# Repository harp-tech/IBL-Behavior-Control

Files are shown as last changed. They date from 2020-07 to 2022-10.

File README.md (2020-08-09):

# IBL Behavior Control (IBL BC)

Repository for the IBL's new behavior control system, based on Harp technology.

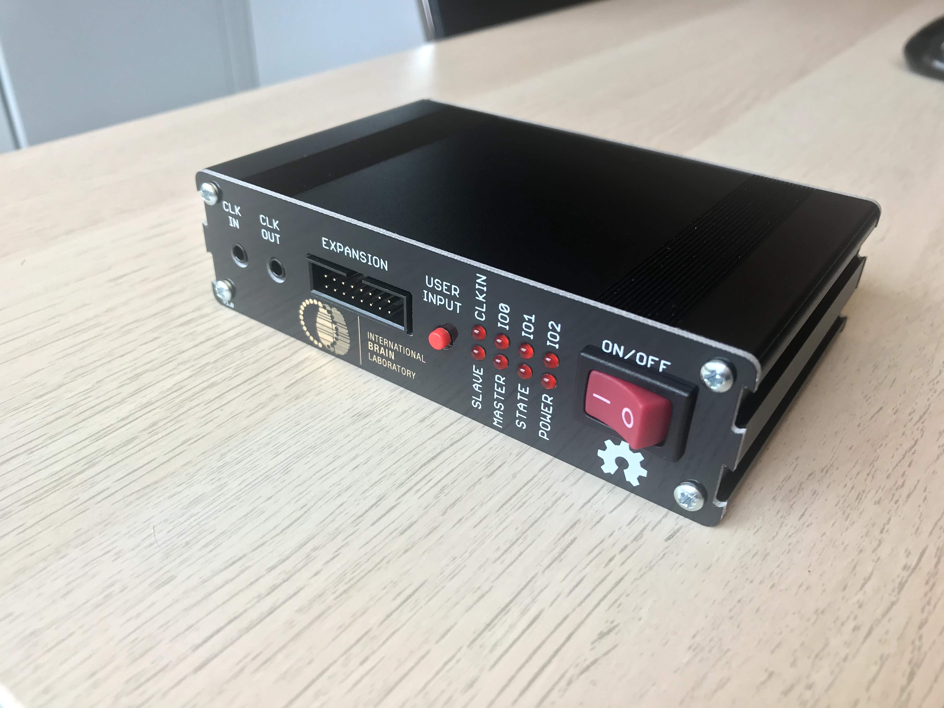
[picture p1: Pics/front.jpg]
DeviceFront


# Documentation

Manuals can be found in the folder *Manuals*

# Licensing

The code, designs, documentation, and photos available in this repository is free: you can redistribute it and/or modify it under the terms of the used license.
Each subdirectory will contain a license or, possibly, a set of licenses if it involves both hardware and software. Check files named LICENSE.

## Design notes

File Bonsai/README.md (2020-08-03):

# Bonsai - IBL Behavior Control Library

Bonsai Library for data acquisition and control of the IBL Behavior Control device.

For edits, you can use the Visual Studio Community Express.
(don't forget to install the .NET package)

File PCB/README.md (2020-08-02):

### Licensing
Copyright Filipe Carvalho 2020

<br />This work is licensed under a <a rel="license" href="http://creativecommons.org/licenses/by-nc-sa/3.0/igo/">Creative Commons Attribution-NonCommercial-ShareAlike 3.0 IGO License</a>.

If your are interested in obtaining a license to sell this device, please contact filipe@open-ephys.org

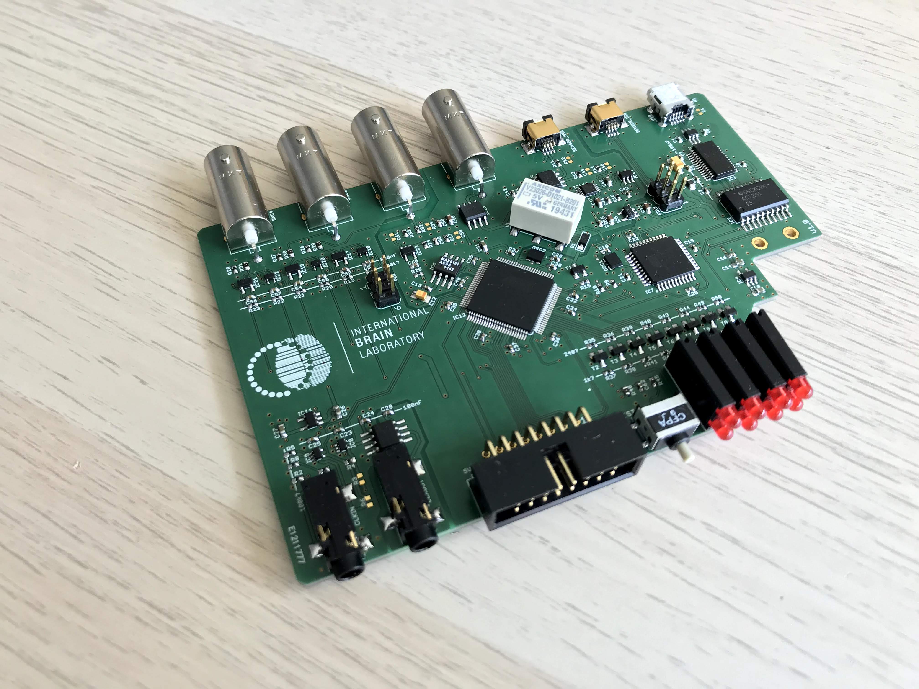
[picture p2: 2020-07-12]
Pics/pcb.jpg

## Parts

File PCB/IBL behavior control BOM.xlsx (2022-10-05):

OEPS PN | Schematic Name | Qtty. | Description | Type | Assembly | Manufacturer PN | Supplier | Supplier PN
OEPS IB1 001 | BNC1, BNC2, BNC3, BNC4 | 4 |  | TH | Yes | 0731000105 | Digi-key | WM5524-ND
OEPS IB1 002 | C1 | 1 | CAP CER 0402 4.7nF 100V ±10% X7R | SMD | Yes | GRM155R72A472KA01D | Mouser | 81-GRM155R72A472KA01
 | C10, C14, C26, C27, C31, C49 | 6 | CAP CER 0603 4.7uF 16V ±10% X5R | SMD | Yes | EMK107ABJ475KA-T | Mouser | 963-EMK107ABJ475KA-T
 | C11, C15, C41, C47, C48 | 5 | CAP CER 0603 10uF 25V ±10% X5R | SMD | Yes | GRM188R61E106KA73D | Mouser | 81-GRM188R61E106KA3D
 | C12 | 1 | SMD TAN 0805 20V 1uF ±10% ESR 6ohm | SMD | Yes | TPSR105K020R6000 | Mouser | 581-TPSR105K020R6000
 | C2, C3, C5, C7, C9, C13, C16, C17, C18, C19, C20, C21, C22, C23, C24, C25, C28, C29, C30, C32, C33, C34, C35, C36, C37, C38, C39, C40, C42, C43, C46, C50, C51, C52, C53, C54, C55, C56, C57, C60, C62 | 41 | CAP CER 0402 100nF 25V ±10% X7R | SMD | Yes | TMK105B7104KVHF | Mouser | 963-TMK105B7104KVHF
 | C4, C6 | 2 | CAP CER 0402 47pF 50V ±5% C0G | SMD | Yes | VJ0402A470JXACW1BC | Mouser | 77-VJ0402A470JXACBC
 | C44, C45, C58, C61 | 4 | - | SMD | DNP | - | - | -
 | C59 | 1 | CAP CER 0402 15nF 16V ±5% X7R | SMD | Yes | GRM155R71C153JA01D | Mouser | 81-GRM155R71C153JA1D
 | C8 | 1 | CAP TAN 1206 4.7uF 16V ±10% | SMD | Yes | TAJA475K016UNJ | Mouser | 581-TAJA475K016UNJ
 | CLKIN, CLKOUT | 2 | STEREO_JACK | SMD | Yes | 35RASMT2BHNTRX | Mouser | 502-35RASMT2BHNTRX
 | D1 | 1 | Schottky diode | SMD | Yes | 1N5819HW-7-F | Mouser | 621-1N5819HW-F
 | IC1 | 1 | ESD protection | SMD | Yes | USBLC6-2SC6Y | Mouser | 511-USBLC6-2SC6Y
 | IC10 | 1 | Digital Isolator | SMD | Yes | SI8610BC-B-IS | Mouser | 634-SI8610BC-B-IS
 | IC12 | 1 | Microcontroller | SMD | Yes | ATXMEGA128A1U-AU | Mouser | 556-ATXMEGA128A1U-AU
 | IC13, IC15 | 2 | OPAMP | SMD | Yes | AD8655ARZ | Mouser | 584-AD8655ARZ
 | IC14 | 1 | LDO 1.8V | SMD | Yes | TCR2EF18,LM(CT | Mouser | 757-TCR2EF18LMCT
 | IC16 | 1 | ADC | SMD | Yes | MCP33151D-10-E/MS | Mouser | 579-CP33151D-10-E/MS
 | IC17, IC19, IC21 | 3 | SINGLE BUS BUFFER GATE | SMD | Yes | SN74LVC1G125DBVR | Mouser | 595-SN74LVC1G125DBVR
 | IC2 | 1 | OCTAL BUFFER/DRIVER | SMD | Yes | SN74ACT241DW | Mouser | 595-SN74ACT241DW
 | IC23 | 1 | OPAMP | SMD | Yes | OPA365AIDBVR | Mouser | 595-OPA365AIDBVR
 | IC3 | 1 | USB TO SERIAL | SMD | Yes | FT232RL-REEL | Mouser | 895-FT232RL
 | IC4, IC11 | 2 | LDO 3.3V 200mA | SMD | Yes | TLV70033DDCR | Mouser | 595-TLV70033DDCR
 | IC5 | 1 | LDO 3.3V 250mA Ultra-Low-Noise | SMD | Yes | LP5907MFX-3.3/NOPB | Mouser | 595-LP5907MFX-3.3NPB
 | IC6 | 1 | REF 2.048V | SMD | Yes | MAX6162AESA+ | Mouser | 700-MAX6162AESA
 | IC7 | 1 | Microcontroller | SMD | Yes | ATXMEGA16A4U-AU | Mouser | 556-ATXMEGA16A4U-AU
 | IC8, IC9, IC18, IC20, IC22 | 5 | SINGLE BUS BUFFER GATE | SMD | Yes | M74VHC1GT126DT1G | Mouser | 863-M74VHC1GT126DT1G
 | L1 | 1 | 40ohms 100MHz 1.5A 0805 SMD | SMD | Yes | MI0805K400R-10 | Mouser | 875-MI0805K400R-10
 | LED0, LED1, LED2 | 4 | LED Circuit Board Indicator | TH | yes | 569-0111-100F | Mouser | 645-569-0111-100F
 | OSC1, OSC2 | 2 | CMOS Oscillator 32MHz 10ppm | SMD | Yes | DSC1001CI5-032.0000 | Mouser | 579-SC1001CI50320000
 | PDI, PDI1 | 2 | 2x3 HEADER | SMD | Yes | 67996-206HLF | Mouser | 649-67996-206HLF
 | R1 | 1 | RES SMD 0402 1MΩ ±1% 62.5mW | SMD | Yes | CR0402-FX-1004GLF | Mouser | 652-CR0402FX-1004GLF
 | R15, R35, R36, R39, R40, R43, R44, R49, R50 | 9 | RES SMD 0402 1kΩ ±1% 62.5mW | SMD | Yes | RC0402FR-071KL | Mouser | 603-RC0402FR-071KL
 | R2, R5, R8, R9, R10, R18, R19, R20, R21, R22, R23, R26, R27, R28 | 14 | RES SMD 0402 100kΩ 1% 100mW | SMD | Yes | ERJ-2RKF1003X | Mouser | 667-ERJ-2RKF1003X
 | R24, R45 | 2 | RES SMD 0402 10kΩ 0.5% 62.5mW | SMD | Yes | ERJ-2RHD1002X | Mouser | 667-ERJ-2RHD1002X
 | R29, R30, R31, R48 | 4 | RES SMD 0603 100Ω 1% 250mW | SMD | Yes | ESR03EZPF1000 | Mouser | 755-ESR03EZPF1000
 | R3, R6, R12, R34 | 4 | - | SMD | DNP | - | - | -
 | R32 | 1 | RES SMD 0402 24kΩ 1% 100mW | SMD | Yes | ERJ-2RKF2402X | Mouser | 667-ERJ-2RKF2402X
 | R33 | 1 | RES SMD 0402 16kΩ 1% 100mW | SMD | Yes | ERJ-2RKF1602X | Mouser | 667-ERJ-2RKF1602X
 | R37, R38, R41, R42, R46, R47, R51, R52 | 8 | RES SMD 0402 240Ω 1% 100mW | SMD | Yes | ERJ-2RKF2700X | Mouser | 667-ERJ-2RKF2700X
 | R4, R14, R17 | 3 | RES SMD 0402 0Ω | SMD | Yes | ERJ-2GE0R00X | Mouser | 667-ERJ-2GE0R00X
 | R7, R11, R13, R16, R25 | 5 | RES SMD 0402 10Ω 1% 100mW | SMD | Yes | ERJ-2RKF10R0X | Mouser | 667-ERJ-2RKF10R0X
 | SENSOR_ANA, SENSOR_DIG | 2 | Sensor plug | SMD | Yes | MQ172X-4PA(31) | Mouser | 798-MQ172X-4PA31
 | SV1 | 1 | CONN HEADER R/A 16POS 2.54MM | SMD | Yes | SBH11-PBPC-D08-RA-BK | Digi-key | S9179-ND
 | T1, T2, T3, T4, T5, T6, T7, T8, T9 | 9 | BJT NPN GP 45V 100mA | SMD | Yes | BC850C,215 | Mouser | 771-BC850C-T/R
 | TEST | 1 | Button | SMD | Yes | CFPA-1FB4-A2T | Digi-key | 563-1246-1-ND
 | U1 | 1 | Relay | SMD | Yes | V23026D1021B201 *X020 | Mouser | 655-V23026D1021XB
 | USB | 1 | Mini-USB connector | SMD | Yes | UX60-MB-5S8 | Mouser | 798-UX60-MB-5S8
 | - | 1 | Mini-USB cable | - | - | 88732-8502 | Mouser | 538-88732-8502
 | - | 1 | Enclosure | - | - | B5-080BK | Farnell | 1418616
 | - | 8 | Thread forming screws, M3, 6.5mm length | - | - |  | Fabory | 26760.029.006 (160411412)
 | - | 4 | Bumper Cylindrical Dome 9.53mm | - | - | SJ-5306-CLEAR-3000/CASE | DigiKey | SJ-5306-CLEAR-3000/CASE-ND

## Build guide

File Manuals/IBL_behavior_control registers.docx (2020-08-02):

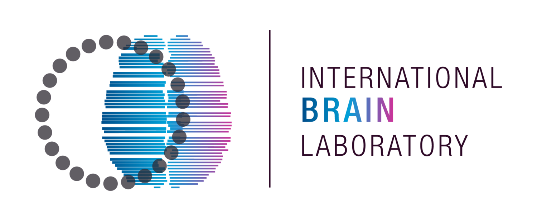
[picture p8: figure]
International Brain Laboratory

IBL Behavior Control - Device Registers Document Version 0.1

1. | Introduction
| The IBL Behavior Control device uses the most recent Harp core. This means that the comunication and synchronism of the device is covered by the Harp ecosistem. Therefore, the device uses registers to interface with the host computer. The user can use the available tools (Python and Bonsai (https://bonsai-rx.org/)) to communicate with the device and write & read from these registers. The purpose of this document is to explain the functionality of each register. If you have doubts, comments or suggestion, please provide them to filipe@open-ephys.org

2. | Registers
2.1 | List of Registers

Table 2-1. List of available Registers

Name | Type | Add | Brief Description
CONFIG | U16 | 32 | Configures the device
DATA_STREAM a) | I16 | 33 | Analog sensor, analog input, rotary encoder, and threshold events
INPUTS a) | U8 | 34 | Contains the state of the digital inputs (IO2) (IO1) (IO0)
INPUT_IO0_CONFIG | U8 | 35 | Configuration of port IO0 when used as digital input
INPUT_IO1_CONFIG | U8 | 36 | Configuration of port IO0 when used as digital input
INPUT_IO2_CONFIG | U8 | 37 | Configuration of port IO0 when used as digital input
OUTPUT_SET | U8 | 38 | Set to logic 1 the port IOx according to bit mask
OUTPUT_CLEAR | U8 | 39 | Clear to logic 0 the port IOx according to bit mask
OUTPUT_TOGGLE | U8 | 40 | Toggles the current logic port IOx according to bit mask
OUTPUT_WRITE | U8 | 41 | Write to the all ports (IO0, IO1 and IO1) at once
ANA_SENSOR_TH0_HIGH | U16 | 42 | Sets the higher threshold 0 for the analog sensor
ANA_SENSOR_TH0_HIGH_MS | U16 | 43 | Sets the number of milliseconds to consider a valid high threshold 0
ANA_SENSOR_TH0_LOW | U16 | 44 | Sets the lower threshold 0 for the analog sensor
ANA_SENSOR_TH0_LOW_MS | U16 | 45 | Sets the number of milliseconds to consider a valid low threshold 0
ANA_SENSOR_TH0_EVT_CONF | U8 | 46 | Configures what to do when the thresholds 0 are crossed
ANA_SENSOR_TH1_HIGH | U16 | 47 | Sets the higher threshold 1 for the analog sensor
ANA_SENSOR_TH1_HIGH_MS | U16 | 48 | Sets the number of milliseconds to consider a valid high threshold 1
ANA_SENSOR_TH1_LOW | U16 | 49 | Sets the lower threshold 1 for the analog sensor
ANA_SENSOR_TH1_LOW_MS | U16 | 50 | Sets the number of milliseconds to consider a valid low threshold 1
ANA_SENSOR_TH1_EVT_CONF | U8 | 51 | Configures what to do when the thresholds 1 are crossed
ANA_INPUT_TH0_HIGH | U16 | 52 | Sets the higher threshold 0 for the analog input
ANA_INPUT_TH0_HIGH_MS | U16 | 53 | Sets the number of milliseconds to consider a valid high threshold 0
ANA_INPUT_TH0_LOW | U16 | 54 | Sets the lower threshold 0 for the analog input
ANA_INPUT_TH0_LOW_MS | U16 | 55 | Sets the number of milliseconds to consider a valid low threshold 0
ANA_INPUT_TH0_EVT_CONF | U8 | 56 | Configures what to do when the thresholds 0 are crossed
ANA_INPUT_TH1_HIGH | U16 | 57 | Sets the higher threshold 1 for the analog input
ANA_INPUT_TH1_HIGH_MS | U16 | 58 | Sets the number of milliseconds to consider a valid high threshold 1
ANA_INPUT_TH1_LOW | U16 | 59 | Sets the lower threshold 1 for the analog input
ANA_INPUT_TH1_LOW_MS | U16 | 60 | Sets the number of milliseconds to consider a valid low threshold 1
ANA_INPUT_TH1_EVT_CONF | U8 | 61 | Configures what to do when the thresholds 1 are crossed
ENCODER_TH0_HIGH | I16 | 62 | Sets the higher threshold 0 for the encoder
ENCODER_TH0_HIGH_MS | U16 | 63 | Sets the number of milliseconds to consider a valid high threshold 0
ENCODER_TH0_LOW | I16 | 64 | Sets the lower threshold 0 for the encoder
ENCODER_TH0_LOW_MS | U16 | 65 | Sets the number of milliseconds to consider a valid low threshold 0
ENCODER_TH0_EVT_CONF | U8 | 66 | Configures what to do when the thresholds 0 are crossed
ENCODER_TH1_HIGH | I16 | 67 | Sets the higher threshold 1 for the encoder
ENCODER_TH1_HIGH_MS | U16 | 68 | Sets the number of milliseconds to consider a valid high threshold 1
ENCODER_TH1_LOW | I16 | 69 | Sets the lower threshold 1 for the encoder
ENCODER_TH1_LOW_MS | U16 | 70 | Sets the number of milliseconds to consider a valid low threshold 1
ENCODER_TH1_EVT_CONF | U8 | 71 | Configures what to do when the thresholds 1 are crossed
TH_ENABLE_EVENTS | U8 | 72 | Enables each event from the thresholds
WRITE_AO | U16 | 73 | Writes to the analog output available on port AO
ENCODER | I16 | 74 | Value of the digital encoder (write this register to 0 to reset the encoder)

a) This register is read only. Writing to this register will issue an error.
2.1.1 | CONFIG

Bit | 15 | 14 | 13 | 12 | 11 | 10 | 9 | 8
| - | DATA_1KHz | DATA_QUIET | IO2_TO_OUTPUT | IO2_TO_INPUT | IO1_TO_OUTPUT | IO1_TO_INPUT | IO0_TO_OUTPUT
Bit | 7 | 6 | 5 | 4 | 3 | 2 | 1 | 0
| IO0_TO_INPUT | COM_TO_TIMESTAMP | COM_TO_MAIN | EN_AI | ANA_INTERNAL_TO_A0 | ANA_SENSOR_TO_A0 | SYNC_TO_SLAVE | SYNC_TO_MASTER

This register is used to configure the device. As a good practice, this register should be the first one to be written.

When writing to one of these bits, the configuration will be executed, i.e., there’s no need to write all the necessary bits at once.

Example: We want to configure the device to enable the Harp Timestamp output, configure the digital IO1 to output and have data streamed at 1 KHz. We have two options (the end result is exactly the same):

Option a) Write all configuration at once

#define B_SYNC_TO_MASTER (1<<0)
#define B_IO1_TO_OUTPUT (1<<10)
#define B_DATA_1KHz (1<<14)

write_register(R_CONFIG, B_SYNC_TO_MASTER | B_IO1_TO_OUTPUT | B_DATA_1KHz);

Option b) Write each configuration individually

write_register(R_CONFIG, B_SYNC_TO_MASTER);
write_register(R_CONFIG, B_IO1_TO_OUTPUT);
write_register(R_CONFIG, B_DATA_1KHz);

- Bits 0 – SYNC_TO_MASTER

The device outputs the internal clock sync into CLKOUT.

Another Harp device can be connected to this bus in order to share the same timestamp base.

- Bit 1 – SYNC_TO_SLAVE

Setting this bit to 1, the device receives the clock sync trough CLKIN and daisy chain it into CLKOUT (to synchronize another Harp device).

- Bit 2 – ANA_SENSOR_TO_A0

Setting this bit to 1, the analog sensor voltage value is sent to port AO. User can use this port to monitor the analog sensor.

- Bit 3 – ANA_INTERNAL_TO_A0

Setting this bit to 1, the internal analog generator is sent to port AO. User can use the register WRITE_A0 to output an analog voltage on this port.

- Bit 4 – EN_AI

Setting this bit to 1, enables the analog input reading on port AI and disables the digital input/output circuitry.

This means that this port is used as an analog port.

- Bit 5 – COM_TO_MAIN

The device has two microcontrollers running internally. One is dedicated to behavior and the other to timing synchronism.

When this bit is set to logic 1, the USB communication is made with the behavior microcontroller.

This feature is used only for firmware update purposes.

- Bit 6 – COM_TO_TIMESTAMP

When this bit is set to logic 1, the USB communication is made with the timing synchronism microcontroller.

This feature is used only for firmware update purposes.

- Bit 7 – IO0_TO_OUTPUT

Setting this bit to 1, configures the port IO0 to be used as a digital output.

- Bit 8 – IO0_TO_INPUT

Setting this bit to 1, configures the port IO0 to be used as a digital input.

- Bit 9 – IO1_TO_OUTPUT

Setting this bit to 1, configures the port IO1 to be used as a digital output.

- Bit 10 – IO1_TO_INPUT

Setting this bit to 1, configures the port IO1 to be used as a digital input.

- Bit 11 – IO2_TO_OUTPUT

Setting this bit to 1, configures the port IO2 to be used as a digital output.

- Bit 12 – IO2_TO_INPUT

Setting this bit to 1, configures the port IO3 to be used as a digital input.

- Bit 13 – DATA_QUIET

The register DATA_STREAM can be sent to the host computer using one of two options. Sent at a frequency of 1000 samples/second or sent only when any of the thresholds is crossed (widely used to screen synchronization).

Setting this bit to 1, configures the device to send the DATA_STREAM register only when a threshold is crossed (on any of the two ways, rising or falling).

- Bit 14 – DATA_1KHz

Setting this bit to 1, configures the device to send the DATA_STREAM register at a frequency of 1000 samples/second.
2.1.2 | DATA_STREAM

This register is an array composed of four words with 16 bits signed.

DATA_STREAM[0] Analog reading from the analog sensor input

DATA_STREAM[1] Analog reading from the AI0 input

DATA_STREAM[2] Rotary encoder’s position

DATA_STREAM[3] Contains a bitmask reflecting the thresholds state

Below, is the DATA_STREAM[3] bitmask.

Bit | 15-6 | 5 | 4 | 3 | 2 | 1 | 0
| - | ENCTH1 | ENCTH0 | AITH1 | AITH0 | ASTH1 | ASTH0

- Bits ASTHx

If this bit is set to 1, it means that the reading of analog sensor input is above the threshold ANA_SENSOR_THx_HIGH for the time configured in ANA_SENSOR_THx_HIGH.

If this bit is clear to 0, it means that the reading of analog sensor input is below the threshold ANA_SENSOR_THx_LOW for the time configured in ANA_SENSOR_THx_LOW.

This bit is always read as 0.

- Bits AITHx

If this bit is set to 1, it means that the reading of analog input is above the threshold ANA_INPUT_THx_HIGH for the time configured in ANA_INPUT_THx_HIGH.

If this bit is clear to 0, it means that the reading of analog input is below the threshold ANA_INPUT_THx_LOW for the time configured in ANA_INPUT_THx_LOW.

- Bits ENCTHx

If this bit is set to 1, it means that the reading of the encoder is above the threshold ENCODER_THx_HIGH for the time configured in ENCODER_THx_HIGH.

If this bit is clear to 0, it means that the reading of the encoder is below the threshold ENCODER_THx_LOW for the time configured in ENCODER_THx_LOW.
2.1.3 | INPUTS
| This register is sent to the host computer according to registers INPUT_IOx_CONFIG. Bit 7 6 5 4 3 2 1 0 - - - - - IO2 IO1 IO0 - Bits 0 – IO0 Contains the digital state of the port IO0. - Bits 1 – IO1 Contains the digital state of the port IO1. - Bits 2 – IO2 Contains the digital state of the port IO2.
2.1.4 | INPUT_IOx_CONFIG It is good practices to keep the bandwidth of the device as low as possible. If what matters is the transition from logic 0 to logic 1 (a camera’s strobe, for instance), the option 1 should be used, and the device will ignore the logic 1 to logic 0 transition.
| Bit 7 6 5 4 3 2 1 0 - - - - - - INPUT_OPTIONS [1:0] - Bits 1:0 – INPUT_OPTIONS [1:0] INPUT_OPTIONS [1:0] Configuration 0 Port IOx input is not used 1 Port IOx input is sensitive to both edges 2 Reserved 3 Reserved
2.1.5 | OUTPUT_SET OUTPUT_CLEAR OUTPUT_TOGGLE OUTPUT_WRITE
| Bit 7 6 5 4 3 2 1 0 - - - - - IO2 IO1 IO0 The action is taking according to the bit mask. Examples: Set only Port IO0 to logic 1: OUTPUT_SET = (1<<0) Set only Port IO2 to logic 1: OUTPUT_SET = (1<<2) Set both Port IO1 and IO2 to logic 1: OUTPUT_SET = (1<<1) | (1<<2) Clear only Port IO1 to logic 0: OUTPUT_CLEAR = (1<<1) Toggle the current logic state of Port IO1: OUTPUT_TOGGLE = (1<<1) Write IO0 to logic 0, IO1 to logic 1 and IO2 to logic 1 (all at the same time): OUTPUT_WRITE = (1<<1) | (1<<2)
2.1.6 | ANA_SENSOR_THx_EVT_CONF ANA_INPUT_THx_EVT_CONF ECNODER_THx_EVT_CONF This register configures if the threshold result is show in the digital outputs.
| Bit 7 6 5 4 3 2 1 0 - - - - - - TH_OPTIONS [1:0] - Bits 1:0 – TH_OPTIONS [1:0] TH_OPTIONS [1:0] Configuration 0 Don’t output the threshold 1 a) Threshold result on IO0 2 Threshold result on IO1 3 Threshold result on IO2 a) This option is not valid when used on registers ANA_INPUT_THx_EVT_CONF.
2.1.7 | TH_ENABLE_EVENTS
| This register allows the user to disable the non-used thresholds. It is recommended to disable the nonused ones! Bit 7 6 5 4 3 2 1 0 - - ENCTH1 ENCTH0 AITH1 AITH0 ASTH1 ASTH0 - Bits 5:0 Writing to logic 0 disables the correspondent threshold. Writing to logic 1 enables the correspondent threshold.

| Version Control
| V0.1 First version released.

IBL Behavior Control | Device Registers 5

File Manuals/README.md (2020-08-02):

### Licensing
Copyright Filipe Carvalho 2020

<br />Este trabalho está licenciado com uma Licença <a rel="license" href="http://creativecommons.org/licenses/by/4.0/">Creative Commons - Atribuição  4.0 Internacional</a>.

#### You are free to:
*Share* — copy and redistribute the material in any medium or format
*Adapt* — remix, transform, and build upon the material for any purpose, even commercially.

#### Under the following terms:
*Attribution* — You must give appropriate credit, provide a link to the license, and indicate if changes were made. You may do so in any reasonable manner, but not in any way that suggests the licensor endorses you or your use.

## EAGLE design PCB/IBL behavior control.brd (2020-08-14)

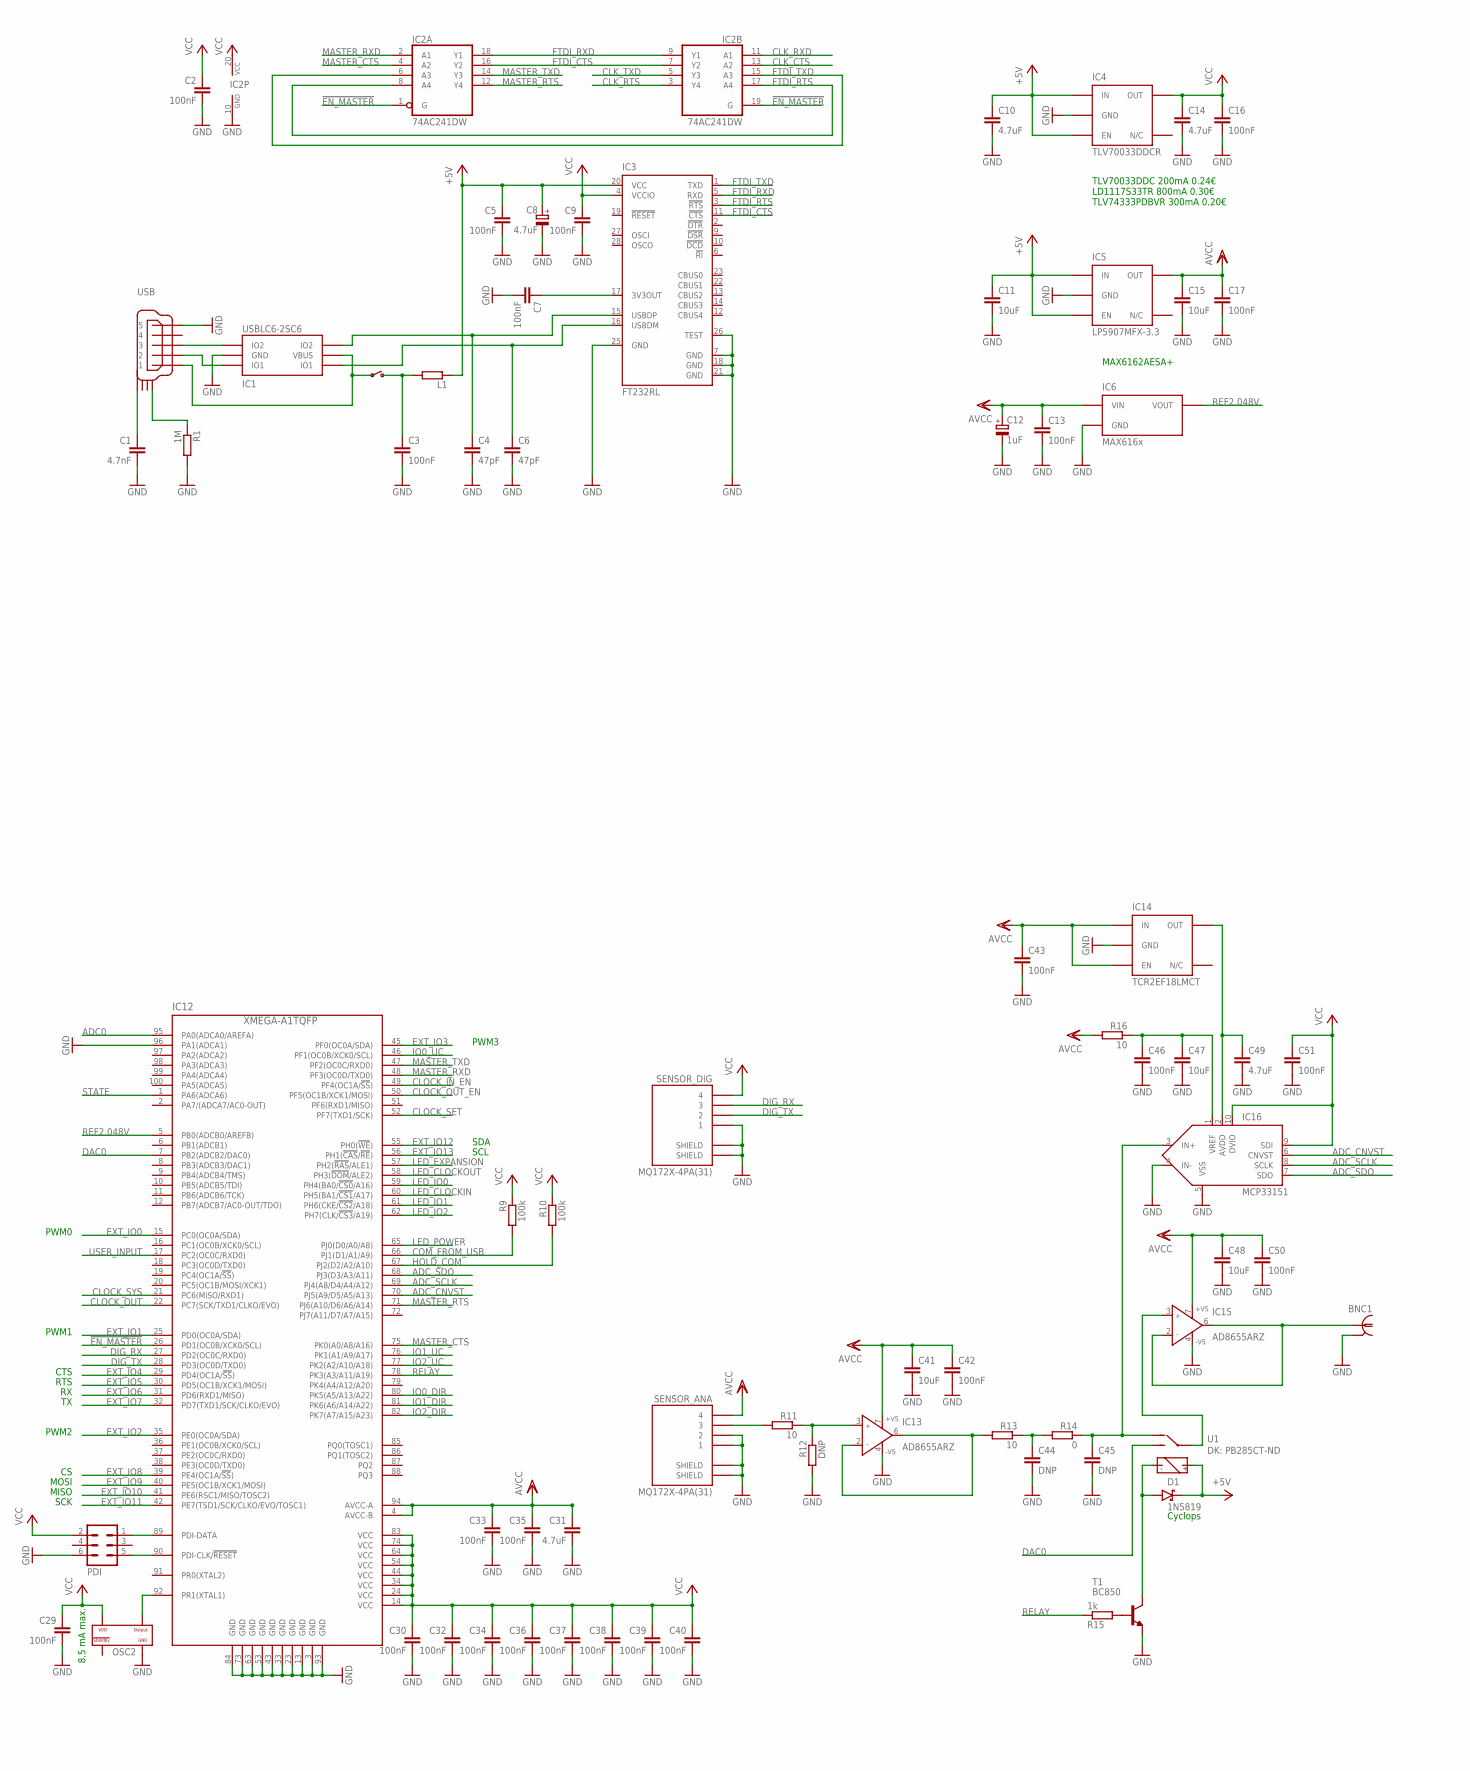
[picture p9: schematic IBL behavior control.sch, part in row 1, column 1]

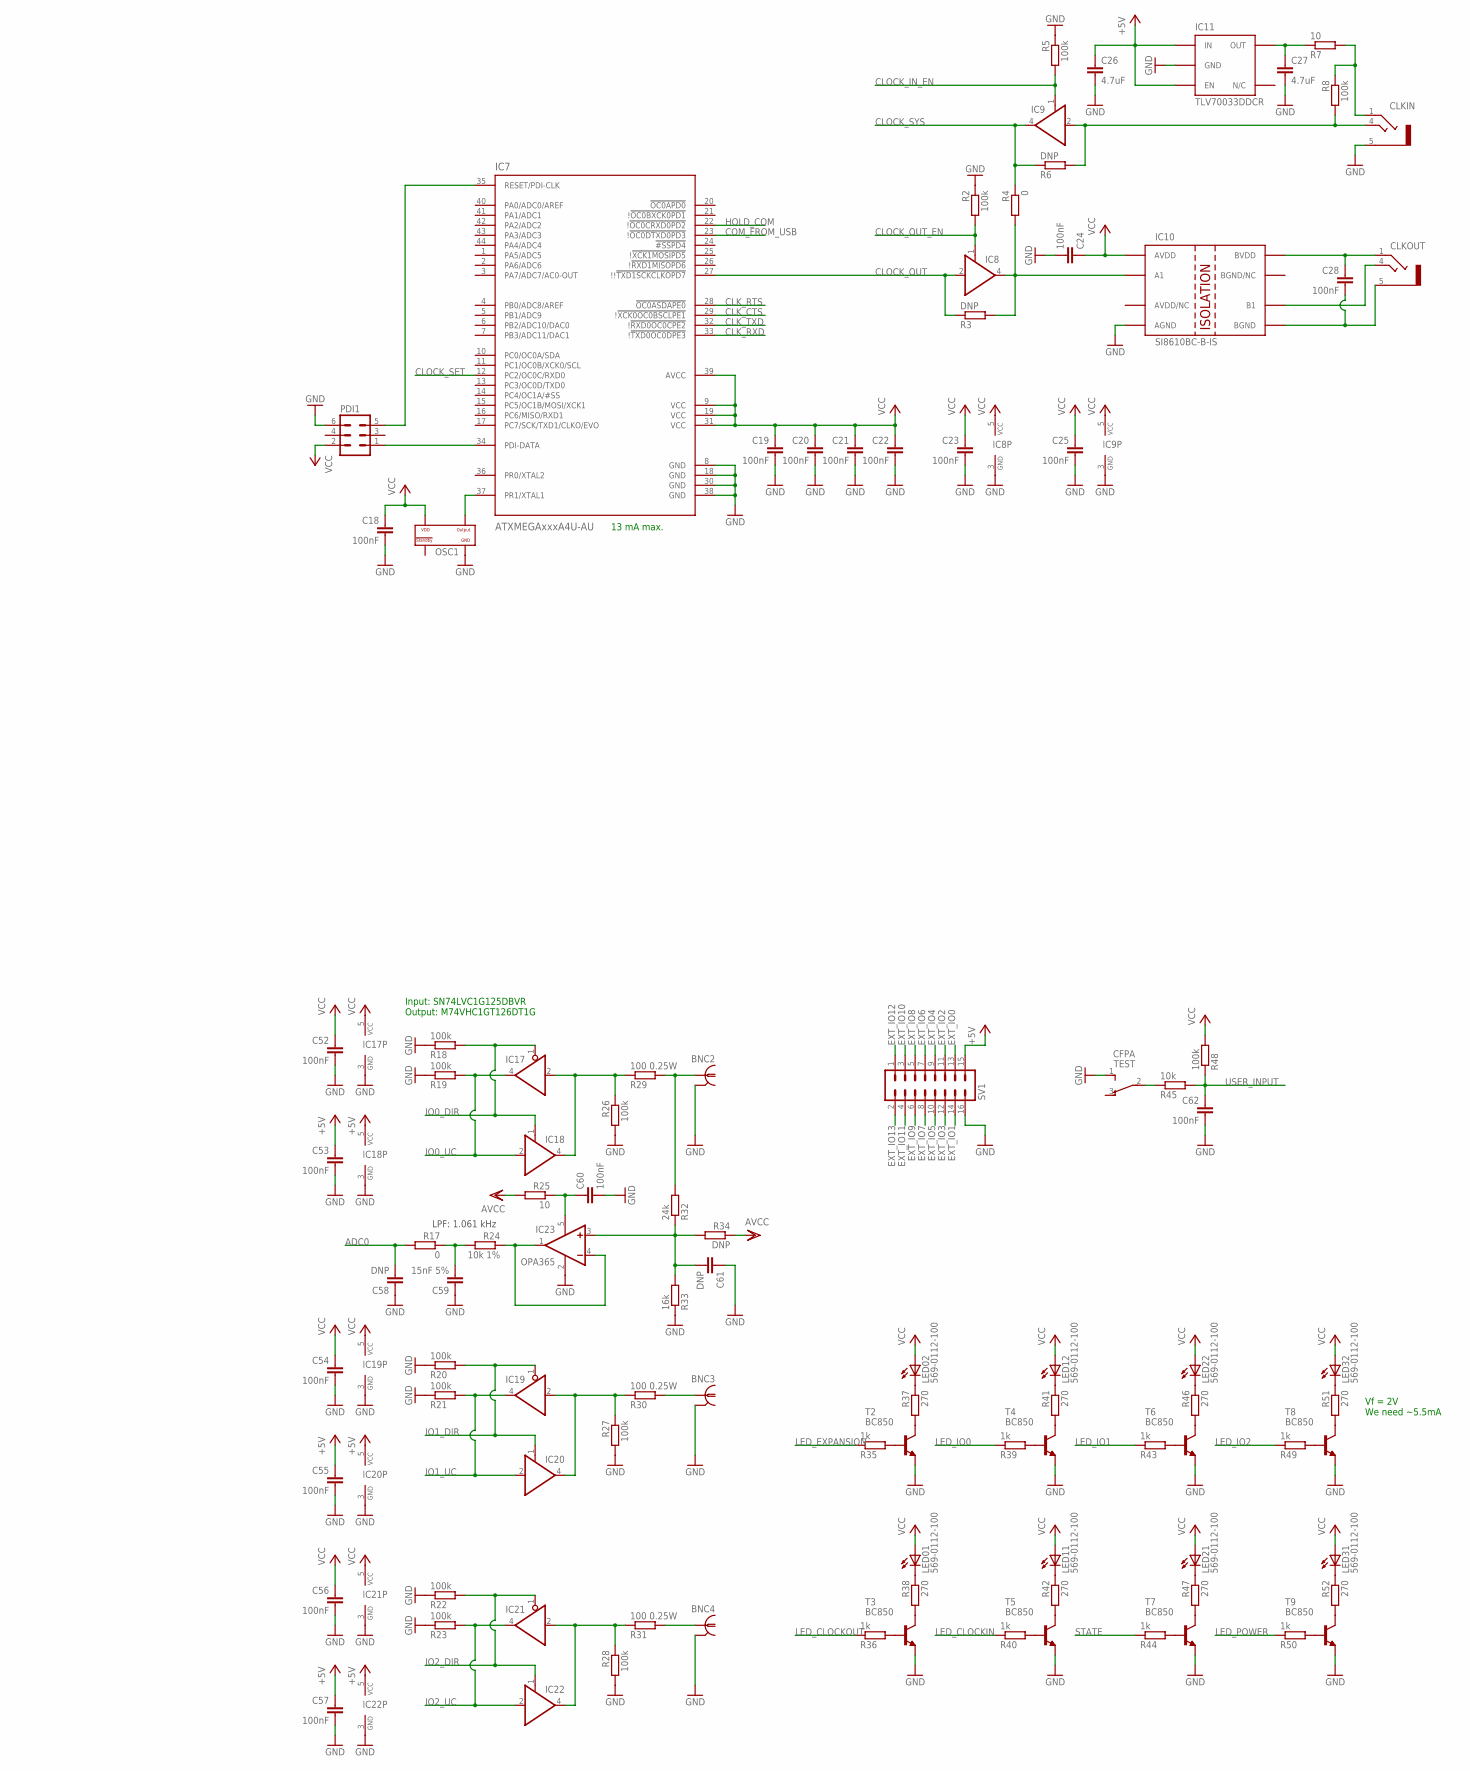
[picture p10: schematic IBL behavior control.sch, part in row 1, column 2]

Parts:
BNC1, BNC2, BNC3, BNC4: BNC_0731000105; 0731000105
C1: 4.7nF; C0402
C2, C3, C5, C7, C9, C13, C16, C17, C18, C19, C20, C21, C22, C23, C24, C25, C28, C29, C30, C32, C33, C34, C35, C36, C37, C38, C39, C40, C42, C43, C46, C50, C51, C52, C53, C54, C55, C56, C57, C60, C62: 100nF; C0402
C4, C6: 47pF; C0402
C8: 4.7uF; A/3216-18W
C10, C14, C26, C27, C31, C49: 4.7uF; C0603
C11, C15, C41, C47, C48: 10uF; C0603
C12: 1uF; R/2012-12R
C44, C45, C58, C61: DNP; C0402
C59: 15nF 5%; C0402
CLKIN: STEREO_JACK; 35RASMT2BHNTRX
CLKOUT: STEREO_JACK; 35RASMT2BHNTRX
D1: 1N5819; SOD123
IC1: USBLC6-2SC6; SOT23-6L
IC2: 74AC241DW; SO20W
IC3: FT232RL; SSOP28
IC4, IC11: TLV70033DDCR; TSOT23-5
IC5: LP5907MFX-3.3; TSOT23-5
IC6: MAX616x; SO-08
IC7: ATXMEGAxxxA4U-AU; QFP80P1200X1200X120-44N
IC8, IC9, IC18, IC20, IC22: 74AHC1G126DCK; SC70-5
IC10: SI8610BC-B-IS; SO-08
IC12: XMEGA-A1TQFP; TQFP100
IC13, IC15: AD8655ARZ; SO8
IC14: TCR2EF18LMCT; TSOT23-5
IC16: MCP33151; MSOP10
IC17, IC19, IC21: 74AHC1G125DBV; SOT23-5
IC23: OPA365; SOT23-5
L1: ???; R0805
LED0, LED1, LED2, LED3: 569-0112-100; 569-011X-X00_LED_ARRAY
OSC1, OSC2: OSCILLATOR; OSCILLATOR_3.2X2.5
PDI, PDI1: MA03-2
R1: 1M; R0402
R2, R5, R8, R9, R10, R18, R19, R20, R21, R22, R23, R26, R27, R28, R48: 100k; R0402
R3, R6, R12, R34: DNP; R0402
R4, R14, R17: 0; R0402
R7, R11, R13, R16, R25: 10; R0402
R15, R35, R36, R39, R40, R43, R44, R49, R50: 1k; R0402
R24: 10k 1%; R0402
R29, R30, R31: 100 0.25W; R0603
R32: 24k; R0402
R33: 16k; R0402
R37, R38, R41, R42, R46, R47, R51, R52: 270; R0402
R45: 10k; R0402
SENSOR_ANA: MQ172X-4PA(31)
SENSOR_DIG: MQ172X-4PA(31)
SV1: ML16L
T1, T2, T3, T4, T5, T6, T7, T8, T9: BC850; SOT23
TEST: CFPA
U1: DK: PB285CT-ND; RELAY
USB: USB_MINI_B; 240-0002-1

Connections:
5VSWITCH: C3.1, L1.2
5VUSB: IC1.P$5 (VBUS), USB.P$1 (1)
!EN_MASTER: IC2.1 (G), IC2.19 (G), IC12.26 (PD1(OC0B/XCK0/SCL))
+5V: C5.1, C8.+, C10.1, C11.1, C26.1, C53.1, C55.1, C57.1, D1.C, IC3.20 (VCC), IC4.1 (IN), IC4.3 (EN), IC5.1 (IN), IC5.3 (EN), IC11.1 (IN), IC11.3 (EN), IC18.5 (VCC), IC20.5 (VCC), IC22.5 (VCC), L1.1, SV1.15, U1.3 (R+)
ADC0: C58.2, IC12.95 (PA0(ADCA0/AREFA)), R17.2
ADC_CNVST: IC12.70 (PJ5(A9/D5/A5/A13)), IC16.6 (CNVST)
ADC_SCLK: IC12.69 (PJ4(A8/D4/A4/A12)), IC16.8 (SCLK)
ADC_SDO: IC12.68 (PJ3(D3/A3/A11)), IC16.7 (SDO)
CLK_CTS: IC2.13 (A2), IC7.29 (!!XCK0OC0BSCLPE1)
CLK_RTS: IC2.3 (Y4), IC7.28 (!OC0ASDAPE0)
CLK_RXD: IC2.11 (A1), IC7.33 (!!TXD0OC0DPE3)
CLK_TXD: IC2.5 (Y3), IC7.32 (!!RXD0OC0CPE2)
CLOCK_IN_EN: IC9.1 (OE), IC12.49 (PF4(OC1A/!SS!)), R5.2
CLOCK_OUT: IC7.27 (!!!TXD1SCKCLKOPD7), IC8.2 (I), IC12.22 (PC7(SCK/TXD1/CLKO/EVO)), R3.1
CLOCK_OUT_EN: IC8.1 (OE), IC12.50 (PF5(OC1B/XCK1/MOSI)), R2.2
CLOCK_SET: IC7.12 (PC2/OC0C/RXD0), IC12.52 (PF7(TXD1/SCK))
CLOCK_SYS: IC9.4 (O), IC12.21 (PC6(MISO/RXD1)), R4.1, R6.1
COM_FROM_USB: IC7.23 (!!OC0DTXD0PD3), IC12.66 (PJ1(D1/A1/A9)), R9.2
DAC0: IC12.7 (PB2(ADCB2/DAC0)), U1.10 (NO)
DIG_RX: IC12.27 (PD2(OC0C/RXD0)), SENSOR_DIG.3
DIG_TX: IC12.28 (PD3(OC0D/TXD0)), SENSOR_DIG.2
EXT_IO0: IC12.15 (PC0(OC0A/SDA)), SV1.13
EXT_IO1: IC12.25 (PD0(OC0A/SDA)), SV1.14
EXT_IO2: IC12.35 (PE0(OC0A/SDA)), SV1.11
EXT_IO3: IC12.45 (PF0(OC0A/SDA)), SV1.12
EXT_IO4: IC12.29 (PD4(OC1A/!SS!)), SV1.9
EXT_IO5: IC12.30 (PD5(OC1B/XCK1/MOSI)), SV1.10
EXT_IO6: IC12.31 (PD6(RXD1/MISO)), SV1.7
EXT_IO7: IC12.32 (PD7(TXD1/SCK/CLKO/EVO)), SV1.8
EXT_IO8: IC12.39 (PE4(OC1A/!SS!)), SV1.5
EXT_IO9: IC12.40 (PE5(OC1B/XCK1/MOSI)), SV1.6
EXT_IO10: IC12.41 (PE6(RSC1/MISO/TOSC2)), SV1.3
EXT_IO11: IC12.42 (PE7(TSD1/SCK/CLKO/EVO/TOSC1)), SV1.4
EXT_IO12: IC12.55 (PH0(!WE!)), SV1.1
EXT_IO13: IC12.56 (PH1(!CAS!/!RE!)), SV1.2
FTDI_CTS: IC2.7 (Y2), IC2.16 (Y2), IC3.11 (!CTS)
FTDI_RTS: IC2.8 (A4), IC2.17 (A4), IC3.3 (!RTS)
FTDI_RXD: IC2.9 (Y1), IC2.18 (Y1), IC3.5 (RXD)
FTDI_TXD: IC2.6 (A3), IC2.15 (A3), IC3.1 (TXD)
GND: BNC1.2, BNC1.3 (2), BNC2.2, BNC2.3 (2), BNC3.2, BNC3.3 (2), BNC4.2, BNC4.3 (2), C1.2, C2.2, C3.2, C4.2, C5.2, C6.2, C7.2, C8.-, C9.2, C10.2, C11.2, C12.-, C13.2, C14.2, C15.2, C16.2, C17.2, C18.2, C19.2, C20.2, C21.2, C22.2, C23.2, C24.2, C25.2, C26.2, C27.2, C29.2, C30.2, C31.2, C32.2, C33.2, C34.2, C35.2, C36.2, C37.2, C38.2, C39.2, C40.2, C41.2, C42.2, C43.2, C44.2, C45.2, C46.2, C47.2, C48.2, C49.2, C50.2, C51.2, C52.2, C53.2, C54.2, C55.2, C56.2, C57.2, C58.1, C59.1, C60.2, C61.1, C62.2, CLKIN.5, IC1.P$2 (GND), IC2.10 (GND), IC3.7 (GND), IC3.18 (GND), IC3.21 (GND), IC3.25 (GND), IC3.26 (TEST), IC4.2 (GND), IC5.2 (GND), IC6.4 (GND), IC7.8 (GND), IC7.18 (GND), IC7.30 (GND), IC7.38 (GND), IC8.3 (GND), IC9.3 (GND), IC10.4 (AGND), IC11.2 (GND), IC12.3 (GND), IC12.13 (GND), IC12.23 (GND), IC12.33 (GND), IC12.43 (GND), IC12.53 (GND), IC12.63 (GND), IC12.73 (GND), IC12.84 (GND), IC12.93 (GND), IC12.96 (PA1(ADCA1)), IC13.4 (-VS), IC14.2 (GND), IC15.4 (-VS), IC16.4 (IN-), IC16.5 (VSS), IC17.3 (GND), IC18.3 (GND), IC19.3 (GND), IC20.3 (GND), IC21.3 (GND), IC22.3 (GND), IC23.2 (V-), OSC1.P$2 (GND), OSC2.P$2 (GND), PDI.6, PDI1.6, R1.2, R2.1, R5.1, R12.2, R18.1, R19.1, R20.1, R21.1, R22.1, R23.1, R26.2, R27.2, R28.2, R33.1, SENSOR_ANA.1, SENSOR_ANA.2, SENSOR_ANA.SHIELD1 (SHIELD), SENSOR_ANA.SHIELD2 (SHIELD), SENSOR_DIG.1, SENSOR_DIG.SHIELD1 (SHIELD), SENSOR_DIG.SHIELD2 (SHIELD), SV1.16, T1.2 (E), T2.2 (E), T3.2 (E), T4.2 (E), T5.2 (E), T6.2 (E), T7.2 (E), T8.2 (E), T9.2 (E), TEST.1 (3), USB.P$5 (5)
GND_ISO: C28.2, CLKOUT.5, IC10.5 (BGND)
HOLD_COM: IC7.22 (!!OC0CRXD0PD2), IC12.67 (PJ2(D2/A2/A10)), R10.2
IO0_ANALOG: C59.2, R17.1, R24.2
IO0_DIR: IC12.80 (PK5(A5/A13/A22)), IC17.1 (OE), IC18.1 (OE), R18.2
IO0_UC: IC12.46 (PF1(OC0B/XCK0/SCL)), IC17.4 (O), IC18.2 (I), R19.2
IO1_DIR: IC12.81 (PK6(A6/A14/A22)), IC19.1 (OE), IC20.1 (OE), R20.2
IO1_UC: IC12.76 (PK1(A1/A9/A17)), IC19.4 (O), IC20.2 (I), R21.2
IO2_DIR: IC12.82 (PK7(A7/A15/A23)), IC21.1 (OE), IC22.1 (OE), R22.2
IO2_UC: IC12.77 (PK2(A2/A10/A18)), IC21.4 (O), IC22.2 (I), R23.2
LED_CLOCKIN: IC12.60 (PH5(BA1/!CS1!/A17)), R40.1
LED_CLOCKOUT: IC12.58 (PH3(!DOM!/ALE2)), R36.1
LED_EXPANSION: IC12.57 (PH2(!RAS!/ALE1)), R35.1
LED_IO0: IC12.59 (PH4(BA0/!CS0!/A16)), R39.1
LED_IO1: IC12.61 (PH6(CKE/!CS2!/A18)), R43.1
LED_IO2: IC12.62 (PH7(CLK/!CS3!/A19)), R49.1
LED_POWER: IC12.65 (PJ0(D0/A0/A8)), R50.1
MASTER_CTS: IC2.4 (A2), IC12.75 (PK0(A0/A8/A16))
MASTER_RTS: IC2.12 (Y4), IC12.71 (PJ6(A10/D6/A6/A14))
MASTER_RXD: IC2.2 (A1), IC12.48 (PF3(OC0D/TXD0))
MASTER_TXD: IC2.14 (Y3), IC12.47 (PF2(OC0C/RXD0))
unnamed: CLKOUT.4, IC10.6 (B1)
unnamed: R35.2, T2.1 (B)
unnamed: LED0.C2 (C), R37.1
unnamed: C28.1, CLKOUT.1, IC10.8 (BVDD)
unnamed: IC17.2 (I), IC18.4 (O), R26.1, R29.1
unnamed: R37.2, T2.3 (C)
unnamed: BNC2.1, R29.2, R32.2
unnamed: IC19.2 (I), IC20.4 (O), R27.1, R30.1
unnamed: BNC3.1, R30.2
unnamed: IC21.2 (I), IC22.4 (O), R28.1, R31.1
unnamed: BNC4.1, R31.2
unnamed: R36.2, T3.1 (B)
unnamed: R43.2, T6.1 (B)
unnamed: R38.2, T3.3 (C)
unnamed: R39.2, T4.1 (B)
unnamed: LED3.C1 (C), R52.1
unnamed: R41.2, T4.3 (C)
unnamed: R40.2, T5.1 (B)
unnamed: R46.2, T6.3 (C)
unnamed: R42.2, T5.3 (C)
unnamed: LED3.C2 (C), R51.1
unnamed: R44.2, T7.1 (B)
unnamed: R47.2, T7.3 (C)
unnamed: R49.2, T8.1 (B)
unnamed: R51.2, T8.3 (C)
unnamed: R50.2, T9.1 (B)
unnamed: R52.2, T9.3 (C)
unnamed: LED1.C2 (C), R41.1
unnamed: LED2.C2 (C), R46.1
unnamed: LED1.C1 (C), R42.1
unnamed: LED2.C1 (C), R47.1
unnamed: R45.1, TEST.2
unnamed: C60.1, IC23.5 (V+), R25.1
unnamed: LED0.C1 (C), R38.1
unnamed: IC13.2 (IN-), IC13.6 (OUT), R13.2
unnamed: C7.1, IC3.17 (3V3OUT)
unnamed: IC13.3 (IN+), R11.1, R12.1
unnamed: IC1.P$1 (IO1), USB.P$2 (2)
unnamed: CLKIN.1, R7.2, R8.1
unnamed: C27.1, IC11.5 (OUT), R7.1
unnamed: IC8.4 (O), IC10.2 (A1), R3.2, R4.2
unnamed: C49.1, IC14.5 (OUT), IC16.2 (AVDD)
unnamed: C44.1, R13.1, R14.2
unnamed: C45.1, IC16.3 (IN+), R14.1, U1.1 (NC)
unnamed: BNC1.1, IC15.2 (IN-), IC15.6 (OUT)
unnamed: C46.1, C47.1, IC16.1 (VREF), R16.1
unnamed: IC1.P$3 (IO2), USB.P$3 (3)
unnamed: IC15.3 (IN+), U1.5 (IN)
unnamed: R11.2, SENSOR_ANA.3
unnamed: R15.2, T1.1 (B)
unnamed: D1.A, T1.3 (C), U1.8 (R-)
unnamed: IC23.1 (OUT), IC23.4 (-IN), R24.1
unnamed: C1.1, USB.SHIELD_4
unnamed: R1.1, USB.SHIELD_1
unnamed: C61.2, IC23.3 (+IN), R32.1, R33.2, R34.2
OSC1: IC12.92 (PR1(XTAL1)), OSC2.P$3 (OUTPUT)
OSC2: IC7.37 (PR1/XTAL1), OSC1.P$3 (OUTPUT)
PDI-CLK: IC7.35 (RESET/PDI-CLK), PDI1.5
PDI-DATA: IC7.34 (PDI-DATA), PDI1.1
PDI_CLK: IC12.90 (PDI-CLK/!RESET), PDI.5
PDI_DATA: IC12.89 (PDI-DATA), PDI.1
REF2.048V: IC6.6 (VOUT), IC12.5 (PB0(ADCB0/AREFB))
RELAY: IC12.78 (PK3(A3/A11/A19)), R15.1
STATE: IC12.1 (PA6(ADCA6)), R44.1
SYNCIN: CLKIN.4, IC9.2 (I), R6.2, R8.2
USBDM: C6.1, IC1.P$6 (IO1), IC3.16 (USBDM)
USBDP: C4.1, IC1.P$4 (IO2), IC3.15 (USBDP)
USER_INPUT: C62.1, IC12.17 (PC2(OC0C/RXD0)), R45.2, R48.1
VCC: C2.1, C9.1, C14.1, C16.1, C18.1, C19.1, C20.1, C21.1, C22.1, C23.1, C24.1, C25.1, C29.1, C30.1, C32.1, C34.1, C36.1, C37.1, C38.1, C39.1, C40.1, C51.1, C52.1, C54.1, C56.1, IC2.20 (VCC), IC3.4 (VCCIO), IC4.5 (OUT), IC7.9 (VCC), IC7.19 (VCC), IC7.31 (VCC), IC7.39 (AVCC), IC8.5 (VCC), IC9.5 (VCC), IC10.1 (AVDD), IC12.14 (VCC), IC12.24 (VCC), IC12.34 (VCC), IC12.44 (VCC), IC12.54 (VCC), IC12.64 (VCC), IC12.74 (VCC), IC12.83 (VCC), IC16.9 (SDI), IC16.10 (DVIO), IC17.5 (VCC), IC19.5 (VCC), IC21.5 (VCC), LED0.A1 (A), LED0.A2 (A), LED1.A1 (A), LED1.A2 (A), LED2.A1 (A), LED2.A2 (A), LED3.A1 (A), LED3.A2 (A), OSC1.P$4 (VDD), OSC2.P$4 (VDD), PDI.2, PDI1.2, R9.1, R10.1, R48.2, SENSOR_DIG.4
VDD: C12.+, C13.1, C15.1, C17.1, C31.1, C33.1, C35.1, C41.1, C42.1, C43.1, C48.1, C50.1, IC5.5 (OUT), IC6.2 (VIN), IC12.4 (AVCC-B), IC12.94 (AVCC-A), IC13.7 (+VS), IC14.1 (IN), IC14.3 (EN), IC15.7 (+VS), R16.2, R25.2, R34.1, SENSOR_ANA.4

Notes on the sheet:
RTS
CTS
PWM2
PWM1
MOSI
MISO
SCK
PWM0
PWM3
SDA
SCL
Input: SN74LVC1G125DBVR Output: M74VHC1GT126DT1G
Vf = 2V We need ~5.5mA
8.5 mA max.
13 mA max.
TLV70033DDC 200mA 0.24€ LD1117S33TR 800mA 0.30€ TLV74333PDBVR 300mA 0.20€
LPF: 1.061 kHz
MAX6162AESA+
Cyclops

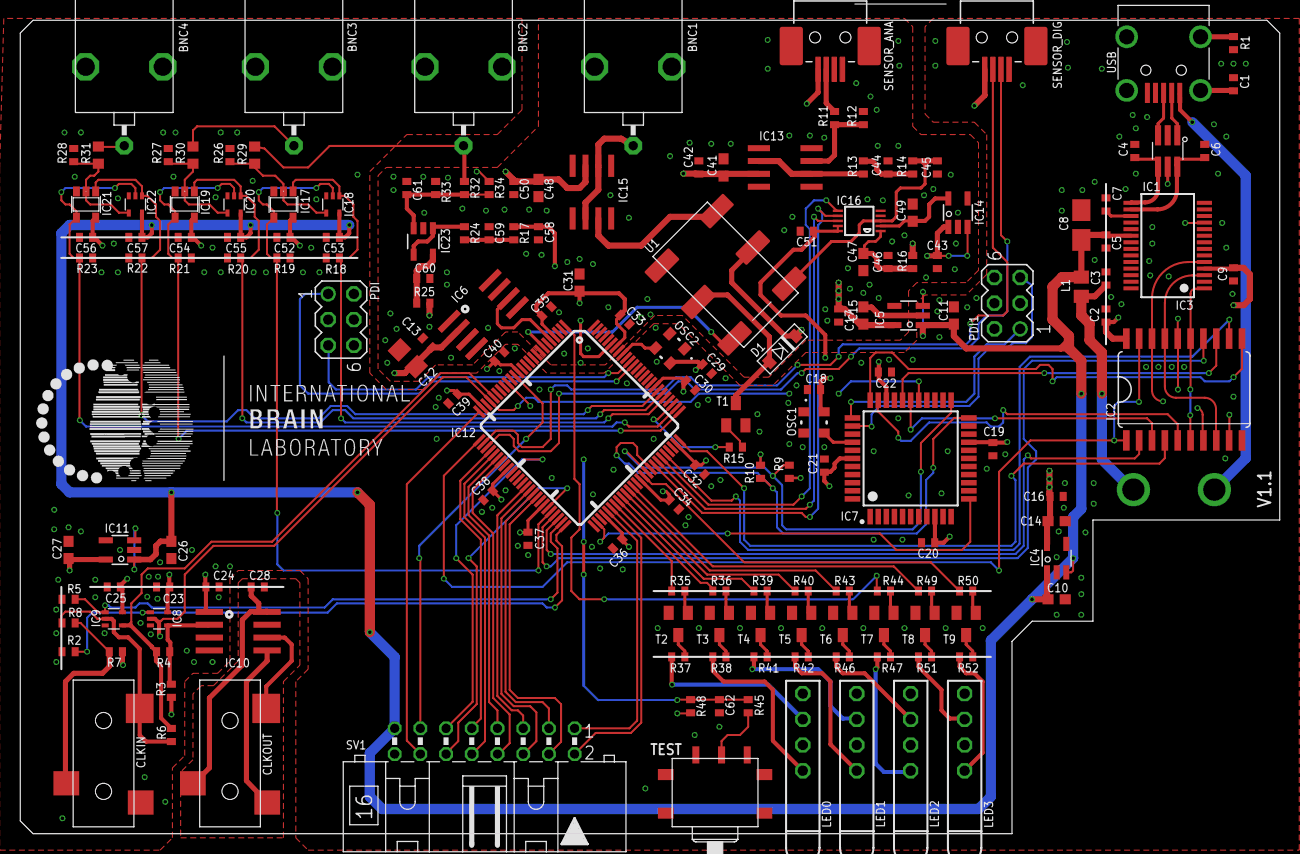
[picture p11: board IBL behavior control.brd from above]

Board: 4 copper layers, 124.5 x 80.4 mm, 168 parts (0 on the bottom side), 130 nets.

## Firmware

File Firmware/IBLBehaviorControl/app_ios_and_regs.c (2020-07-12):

#include <avr/io.h>
#include "hwbp_core_types.h"
#include "app_ios_and_regs.h"

/************************************************************************/
/* Configure and initialize IOs                                         */
/************************************************************************/
void init_ios(void)
{	/* Configure input pins */
	io_pin2in(&PORTJ, 3, PULL_IO_TRISTATE, SENSE_IO_EDGES_BOTH);         // ADC_SDO
	io_pin2in(&PORTC, 2, PULL_IO_TRISTATE, SENSE_IO_EDGES_BOTH);         // USER
	io_pin2in(&PORTF, 1, PULL_IO_TRISTATE, SENSE_IO_EDGES_BOTH);         // IO0
	io_pin2in(&PORTK, 1, PULL_IO_TRISTATE, SENSE_IO_EDGES_BOTH);         // IO1
	io_pin2in(&PORTK, 2, PULL_IO_TRISTATE, SENSE_IO_EDGES_BOTH);         // IO2

	/* Configure input interrupts */
	io_set_int(&PORTC, INT_LEVEL_LOW, 0, (1<<2), false);                 // USER
	io_set_int(&PORTF, INT_LEVEL_LOW, 0, (1<<1), false);                 // IO0
	io_set_int(&PORTK, INT_LEVEL_LOW, 0, (1<<1), false);                 // IO1
	io_set_int(&PORTK, INT_LEVEL_LOW, 1, (1<<2), false);                 // IO2

	/* Configure output pins */
	io_pin2out(&PORTF, 4, OUT_IO_DIGITAL, IN_EN_IO_EN);                  // CLOCK_IN_EN
	io_pin2out(&PORTF, 5, OUT_IO_DIGITAL, IN_EN_IO_EN);                  // CLOCK_OUT_EN
	io_pin2out(&PORTK, 3, OUT_IO_DIGITAL, IN_EN_IO_EN);                  // RELAY
	io_pin2out(&PORTJ, 4, OUT_IO_DIGITAL, IN_EN_IO_EN);                  // ADC_SCLK
	io_pin2out(&PORTJ, 5, OUT_IO_DIGITAL, IN_EN_IO_EN);                  // ADC_CNVST
	io_pin2out(&PORTD, 1, OUT_IO_DIGITAL, IN_EN_IO_EN);                  // EN_MASTER
	io_pin2out(&PORTH, 2, OUT_IO_DIGITAL, IN_EN_IO_EN);                  // LED_CLKIN
	io_pin2out(&PORTH, 4, OUT_IO_DIGITAL, IN_EN_IO_EN);                  // LED_IO0
	io_pin2out(&PORTH, 6, OUT_IO_DIGITAL, IN_EN_IO_EN);                  // LED_IO1
	io_pin2out(&PORTH, 7, OUT_IO_DIGITAL, IN_EN_IO_EN);                  // LED_IO2
	io_pin2out(&PORTH, 3, OUT_IO_DIGITAL, IN_EN_IO_EN);                  // LED_SLAVE
	io_pin2out(&PORTH, 5, OUT_IO_DIGITAL, IN_EN_IO_EN);                  // LED_MASTER
	io_pin2out(&PORTA, 6, OUT_IO_DIGITAL, IN_EN_IO_EN);                  // LED_STATE
	io_pin2out(&PORTJ, 0, OUT_IO_DIGITAL, IN_EN_IO_EN);                  // LED_POWER
	io_pin2out(&PORTF, 1, OUT_IO_DIGITAL, IN_EN_IO_EN);                  // IO0
	io_pin2out(&PORTK, 1, OUT_IO_DIGITAL, IN_EN_IO_EN);                  // IO1
	io_pin2out(&PORTK, 2, OUT_IO_DIGITAL, IN_EN_IO_EN);                  // IO2
	io_pin2out(&PORTK, 5, OUT_IO_DIGITAL, IN_EN_IO_EN);                  // IO0_DIR
	io_pin2out(&PORTK, 6, OUT_IO_DIGITAL, IN_EN_IO_EN);                  // IO1_DIR
	io_pin2out(&PORTK, 7, OUT_IO_DIGITAL, IN_EN_IO_EN);                  // IO2_DIR

	/* Initialize output pins */
	clr_CLOCK_IN_EN;
	clr_CLOCK_OUT_EN;
	clr_RELAY;
	clr_ADC_SCLK;
	clr_ADC_CNVST;
	clr_EN_MASTER;
	clr_LED_CLKIN;
	clr_LED_IO0;
	clr_LED_IO1;
	clr_LED_IO2;
	clr_LED_SLAVE;
	clr_LED_MASTER;
	clr_LED_STATE;
	clr_LED_POWER;
	clr_IO0;
	clr_IO1;
	clr_IO2;
	clr_IO0_DIR;
	clr_IO1_DIR;
	clr_IO2_DIR;
}

/************************************************************************/
/* Registers' stuff                                                     */
/************************************************************************/
AppRegs app_regs;

uint8_t app_regs_type[] = {
	TYPE_U16,
	TYPE_I16,
	TYPE_U8,
	TYPE_U8,
	TYPE_U8,
	TYPE_U8,
	TYPE_U8,
	TYPE_U8,
	TYPE_U8,
	TYPE_U8,
	TYPE_U16,
	TYPE_U16,
	TYPE_U16,
	TYPE_U16,
	TYPE_U8,
	TYPE_U16,
	TYPE_U16,
	TYPE_U16,
	TYPE_U16,
	TYPE_U8,
	TYPE_U16,
	TYPE_U16,
	TYPE_U16,
	TYPE_U16,
	TYPE_U8,
	TYPE_U16,
	TYPE_U16,
	TYPE_U16,
	TYPE_U16,
	TYPE_U8,
	TYPE_I16,
	TYPE_U16,
	TYPE_I16,
	TYPE_U16,
	TYPE_U8,
	TYPE_I16,
	TYPE_U16,
	TYPE_I16,
	TYPE_U16,
	TYPE_U8,
	TYPE_U8,
	TYPE_U16,
	TYPE_I16
};

uint16_t app_regs_n_elements[] = {
	1,
	4,
	1,
	1,
	1,
	1,
	1,
	1,
	1,
	1,
	1,
	1,
	1,
	1,
	1,
	1,
	1,
	1,
	1,
	1,
	1,
	1,
	1,
	1,
	1,
	1,
	1,
	1,
	1,
	1,
	1,
	1,
	1,
	1,
	1,
	1,
	1,
	1,
	1,
	1,
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
};

uint8_t *app_regs_pointer[] = {
	(uint8_t*)(&app_regs.REG_CONFIG),
	(uint8_t*)(app_regs.REG_DATA_STREAM),
	(uint8_t*)(&app_regs.REG_INPUTS),
	(uint8_t*)(&app_regs.REG_INPUT_IO0_CONFIG),
	(uint8_t*)(&app_regs.REG_INPUT_IO1_CONFIG),
	(uint8_t*)(&app_regs.REG_INPUT_IO2_CONFIG),
	(uint8_t*)(&app_regs.REG_OUTPUT_SET),
	(uint8_t*)(&app_regs.REG_OUTPUT_CLEAR),
	(uint8_t*)(&app_regs.REG_OUTPUT_TOGGLE),
	(uint8_t*)(&app_regs.REG_OUTPUT_WRITE),
	(uint8_t*)(&app_regs.REG_ANA_SENSOR_TH0_HIGH),
	(uint8_t*)(&app_regs.REG_ANA_SENSOR_TH0_HIGH_MS),
	(uint8_t*)(&app_regs.REG_ANA_SENSOR_TH0_LOW),
	(uint8_t*)(&app_regs.REG_ANA_SENSOR_TH0_LOW_MS),
	(uint8_t*)(&app_regs.REG_ANA_SENSOR_TH0_EVT_CONF),
	(uint8_t*)(&app_regs.REG_ANA_SENSOR_TH1_HIGH),
	(uint8_t*)(&app_regs.REG_ANA_SENSOR_TH1_HIGH_MS),
	(uint8_t*)(&app_regs.REG_ANA_SENSOR_TH1_LOW),
	(uint8_t*)(&app_regs.REG_ANA_SENSOR_TH1_LOW_MS),
	(uint8_t*)(&app_regs.REG_ANA_SENSOR_TH1_EVT_CONF),
	(uint8_t*)(&app_regs.REG_ANA_INPUT_TH0_HIGH),
	(uint8_t*)(&app_regs.REG_ANA_INPUT_TH0_HIGH_MS),
	(uint8_t*)(&app_regs.REG_ANA_INPUT_TH0_LOW),
	(uint8_t*)(&app_regs.REG_ANA_INPUT_TH0_LOW_MS),
	(uint8_t*)(&app_regs.REG_ANA_INPUT_TH0_EVT_CONF),
	(uint8_t*)(&app_regs.REG_ANA_INPUT_TH1_HIGH),
	(uint8_t*)(&app_regs.REG_ANA_INPUT_TH1_HIGH_MS),
	(uint8_t*)(&app_regs.REG_ANA_INPUT_TH1_LOW),
	(uint8_t*)(&app_regs.REG_ANA_INPUT_TH1_LOW_MS),
	(uint8_t*)(&app_regs.REG_ANA_INPUT_TH1_EVT_CONF),
	(uint8_t*)(&app_regs.REG_ENCODER_TH0_HIGH),
	(uint8_t*)(&app_regs.REG_ENCODER_TH0_HIGH_MS),
	(uint8_t*)(&app_regs.REG_ENCODER_TH0_LOW),
	(uint8_t*)(&app_regs.REG_ENCODER_TH0_LOW_MS),
	(uint8_t*)(&app_regs.REG_ENCODER_TH0_EVT_CONF),
	(uint8_t*)(&app_regs.REG_ENCODER_TH1_HIGH),
	(uint8_t*)(&app_regs.REG_ENCODER_TH1_HIGH_MS),
	(uint8_t*)(&app_regs.REG_ENCODER_TH1_LOW),
	(uint8_t*)(&app_regs.REG_ENCODER_TH1_LOW_MS),
	(uint8_t*)(&app_regs.REG_ENCODER_TH1_EVT_CONF),
	(uint8_t*)(&app_regs.REG_TH_ENABLE_EVENTS),
	(uint8_t*)(&app_regs.REG_WRITE_AO),
	(uint8_t*)(&app_regs.REG_ENCODER)
};

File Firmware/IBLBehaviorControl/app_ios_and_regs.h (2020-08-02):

#ifndef _APP_IOS_AND_REGS_H_
#define _APP_IOS_AND_REGS_H_
#include "cpu.h"

void init_ios(void);
/************************************************************************/
/* Definition of input pins                                             */
/************************************************************************/
// ADC_SDO                Description: Data from the analog sensor's ADC
// USER                   Description: USER's input button
// IO0                    Description: IO0 as input
// IO1                    Description: IO1 as input 
// IO2                    Description: IO2 as input 

#define read_ADC_SDO read_io(PORTJ, 3)          // ADC_SDO
#define read_USER read_io(PORTC, 2)             // USER
#define read_IO0 read_io(PORTF, 1)              // IO0
#define read_IO1 read_io(PORTK, 1)              // IO1
#define read_IO2 read_io(PORTK, 2)              // IO2

/************************************************************************/
/* Definition of output pins                                            */
/************************************************************************/
// CLOCK_IN_EN            Description: Device is sync from the external CLKIN
// CLOCK_OUT_EN           Description: Device syncs devices trough CLKOUT
// RELAY                  Description: Sends analog sensor to port A0
// ADC_SCLK               Description: Clock of the analog sensor's ADC
// ADC_CNVST              Description: Conversion of the analog sensor's ADC
// EN_MASTER              Description: Selects the comunication flow
// LED_CLKIN              Description: Drives the CLKIN LED
// LED_IO0                Description: Drives the IO0 LED
// LED_IO1                Description: Drives the IO1 LED
// LED_IO2                Description: Drives the IO2 LED
// LED_SLAVE              Description: Drives the SLAVE LED
// LED_MASTER             Description: Drives the MASTER LED
// LED_STATE              Description: Drives the STATE LED
// LED_POWER              Description: Drives the POWER LED
// IO0                    Description: IO0 as output
// IO1                    Description: IO1 as output
// IO2                    Description: IO2 as output
// IO0_DIR                Description: Configures IO0 direction
// IO1_DIR                Description: Configures IO1 direction
// IO2_DIR                Description: Configures I20 direction

/* CLOCK_IN_EN */
#define set_CLOCK_IN_EN set_io(PORTF, 4)
#define clr_CLOCK_IN_EN clear_io(PORTF, 4)
#define tgl_CLOCK_IN_EN toggle_io(PORTF, 4)
#define read_CLOCK_IN_EN read_io(PORTF, 4)

/* CLOCK_OUT_EN */
#define set_CLOCK_OUT_EN set_io(PORTF, 5)
#define clr_CLOCK_OUT_EN clear_io(PORTF, 5)
#define tgl_CLOCK_OUT_EN toggle_io(PORTF, 5)
#define read_CLOCK_OUT_EN read_io(PORTF, 5)

/* RELAY */
#define set_RELAY set_io(PORTK, 3)
#define clr_RELAY clear_io(PORTK, 3)
#define tgl_RELAY toggle_io(PORTK, 3)
#define read_RELAY read_io(PORTK, 3)

/* ADC_SCLK */
#define set_ADC_SCLK set_io(PORTJ, 4)
#define clr_ADC_SCLK clear_io(PORTJ, 4)
#define tgl_ADC_SCLK toggle_io(PORTJ, 4)
#define read_ADC_SCLK read_io(PORTJ, 4)

/* ADC_CNVST */
#define set_ADC_CNVST set_io(PORTJ, 5)
#define clr_ADC_CNVST clear_io(PORTJ, 5)
#define tgl_ADC_CNVST toggle_io(PORTJ, 5)
#define read_ADC_CNVST read_io(PORTJ, 5)

/* EN_MASTER */
#define set_EN_MASTER set_io(PORTD, 1)
#define clr_EN_MASTER clear_io(PORTD, 1)
#define tgl_EN_MASTER toggle_io(PORTD, 1)
#define read_EN_MASTER read_io(PORTD, 1)

/* LED_CLKIN */
#define set_LED_CLKIN set_io(PORTH, 2)
#define clr_LED_CLKIN clear_io(PORTH, 2)
#define tgl_LED_CLKIN toggle_io(PORTH, 2)
#define read_LED_CLKIN read_io(PORTH, 2)

/* LED_IO0 */
#define set_LED_IO0 set_io(PORTH, 4)
#define clr_LED_IO0 clear_io(PORTH, 4)
#define tgl_LED_IO0 toggle_io(PORTH, 4)
#define read_LED_IO0 read_io(PORTH, 4)

/* LED_IO1 */
#define set_LED_IO1 set_io(PORTH, 6)
#define clr_LED_IO1 clear_io(PORTH, 6)
#define tgl_LED_IO1 toggle_io(PORTH, 6)
#define read_LED_IO1 read_io(PORTH, 6)

/* LED_IO2 */
#define set_LED_IO2 set_io(PORTH, 7)
#define clr_LED_IO2 clear_io(PORTH, 7)
#define tgl_LED_IO2 toggle_io(PORTH, 7)
#define read_LED_IO2 read_io(PORTH, 7)

/* LED_SLAVE */
#define set_LED_SLAVE set_io(PORTH, 3)
#define clr_LED_SLAVE clear_io(PORTH, 3)
#define tgl_LED_SLAVE toggle_io(PORTH, 3)
#define read_LED_SLAVE read_io(PORTH, 3)

/* LED_MASTER */
#define set_LED_MASTER set_io(PORTH, 5)
#define clr_LED_MASTER clear_io(PORTH, 5)
#define tgl_LED_MASTER toggle_io(PORTH, 5)
#define read_LED_MASTER read_io(PORTH, 5)

/* LED_STATE */
#define set_LED_STATE set_io(PORTA, 6)
#define clr_LED_STATE clear_io(PORTA, 6)
#define tgl_LED_STATE toggle_io(PORTA, 6)
#define read_LED_STATE read_io(PORTA, 6)

/* LED_POWER */
#define set_LED_POWER set_io(PORTJ, 0)
#define clr_LED_POWER clear_io(PORTJ, 0)
#define tgl_LED_POWER toggle_io(PORTJ, 0)
#define read_LED_POWER read_io(PORTJ, 0)

/* IO0 */
#define set_IO0 set_io(PORTF, 1)
#define clr_IO0 clear_io(PORTF, 1)
#define tgl_IO0 toggle_io(PORTF, 1)
#define read_IO0 read_io(PORTF, 1)

/* IO1 */
#define set_IO1 set_io(PORTK, 1)
#define clr_IO1 clear_io(PORTK, 1)
#define tgl_IO1 toggle_io(PORTK, 1)
#define read_IO1 read_io(PORTK, 1)

/* IO2 */
#define set_IO2 set_io(PORTK, 2)
#define clr_IO2 clear_io(PORTK, 2)
#define tgl_IO2 toggle_io(PORTK, 2)
#define read_IO2 read_io(PORTK, 2)

/* IO0_DIR */
#define set_IO0_DIR set_io(PORTK, 5)
#define clr_IO0_DIR clear_io(PORTK, 5)
#define tgl_IO0_DIR toggle_io(PORTK, 5)
#define read_IO0_DIR read_io(PORTK, 5)

/* IO1_DIR */
#define set_IO1_DIR set_io(PORTK, 6)
#define clr_IO1_DIR clear_io(PORTK, 6)
#define tgl_IO1_DIR toggle_io(PORTK, 6)
#define read_IO1_DIR read_io(PORTK, 6)

/* IO2_DIR */
#define set_IO2_DIR set_io(PORTK, 7)
#define clr_IO2_DIR clear_io(PORTK, 7)
#define tgl_IO2_DIR toggle_io(PORTK, 7)
#define read_IO2_DIR read_io(PORTK, 7)


/************************************************************************/
/* Registers' structure                                                 */
/************************************************************************/
typedef struct
{
	uint16_t REG_CONFIG;
	int16_t REG_DATA_STREAM[4];
	uint8_t REG_INPUTS;
	uint8_t REG_INPUT_IO0_CONFIG;
	uint8_t REG_INPUT_IO1_CONFIG;
	uint8_t REG_INPUT_IO2_CONFIG;
	uint8_t REG_OUTPUT_SET;
	uint8_t REG_OUTPUT_CLEAR;
	uint8_t REG_OUTPUT_TOGGLE;
	uint8_t REG_OUTPUT_WRITE;
	uint16_t REG_ANA_SENSOR_TH0_HIGH;
	uint16_t REG_ANA_SENSOR_TH0_HIGH_MS;
	uint16_t REG_ANA_SENSOR_TH0_LOW;
	uint16_t REG_ANA_SENSOR_TH0_LOW_MS;
	uint8_t REG_ANA_SENSOR_TH0_EVT_CONF;
	uint16_t REG_ANA_SENSOR_TH1_HIGH;
	uint16_t REG_ANA_SENSOR_TH1_HIGH_MS;
	uint16_t REG_ANA_SENSOR_TH1_LOW;
	uint16_t REG_ANA_SENSOR_TH1_LOW_MS;
	uint8_t REG_ANA_SENSOR_TH1_EVT_CONF;
	uint16_t REG_ANA_INPUT_TH0_HIGH;
	uint16_t REG_ANA_INPUT_TH0_HIGH_MS;
	uint16_t REG_ANA_INPUT_TH0_LOW;
	uint16_t REG_ANA_INPUT_TH0_LOW_MS;
	uint8_t REG_ANA_INPUT_TH0_EVT_CONF;
	uint16_t REG_ANA_INPUT_TH1_HIGH;
	uint16_t REG_ANA_INPUT_TH1_HIGH_MS;
	uint16_t REG_ANA_INPUT_TH1_LOW;
	uint16_t REG_ANA_INPUT_TH1_LOW_MS;
	uint8_t REG_ANA_INPUT_TH1_EVT_CONF;
	int16_t REG_ENCODER_TH0_HIGH;
	uint16_t REG_ENCODER_TH0_HIGH_MS;
	int16_t REG_ENCODER_TH0_LOW;
	uint16_t REG_ENCODER_TH0_LOW_MS;
	uint8_t REG_ENCODER_TH0_EVT_CONF;
	int16_t REG_ENCODER_TH1_HIGH;
	uint16_t REG_ENCODER_TH1_HIGH_MS;
	int16_t REG_ENCODER_TH1_LOW;
	uint16_t REG_ENCODER_TH1_LOW_MS;
	uint8_t REG_ENCODER_TH1_EVT_CONF;
	uint8_t REG_TH_ENABLE_EVENTS;
	uint16_t REG_WRITE_AO;
	int16_t REG_ENCODER;
} AppRegs;
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

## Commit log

2020-07-12 Added firmware files.
    [registers.xls]
2020-07-12 Added PCB files.
    [IBL behavior control BOM.xlsx, IBL behavior control.brd, IBL behavior control.sch, panel back.brd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]
2020-07-12 Added photos of the device.
2020-07-12 Added photo of the device to README file.
2020-08-02 Updated registers' default and improved LED indication.
2020-08-02 Corrected register CONFIG and implemented the digital inputs' events.
    [registers.xls]
2020-08-02 Added images of the logos used in the PCBs and updated the PCBs' license to NonCommercial.
2020-08-09 Minor edit on README.md and corrected device ID.
2020-08-09 Fixed front panel measurements.
    [panel front.brd]
2020-08-14 Removed common values silkscreen
    [IBL behavior control.brd]
2022-10-05 Replaced an obsolete component.
    [IBL behavior control BOM.xlsx]
2022-10-05 Minor correction.
    [registers.xls]
